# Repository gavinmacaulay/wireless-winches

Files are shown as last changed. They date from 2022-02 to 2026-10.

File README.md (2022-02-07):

# Wireless echosounder calibration winch system
 
This repository contains the manual for the Aqualyd Wireless Echosounder Calibration Winch System. A pdf of the latest version is available [here](https://github.com/gavinmacaulay/wireless-winches/blob/main/generated-docs/User%20and%20Technical%20Manual.pdf?raw=true).

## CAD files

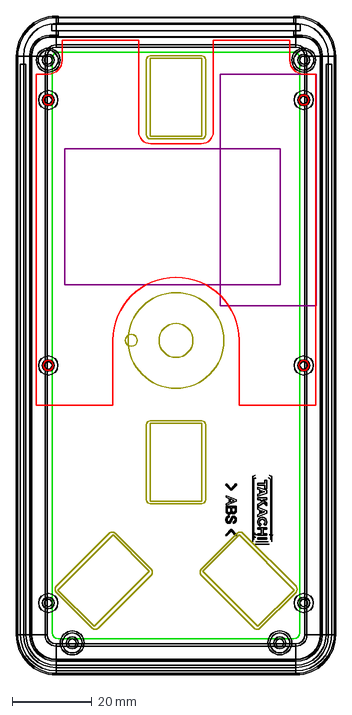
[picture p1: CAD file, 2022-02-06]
schematics/controller cut layout.dxf
80.0 x 165.0 mm

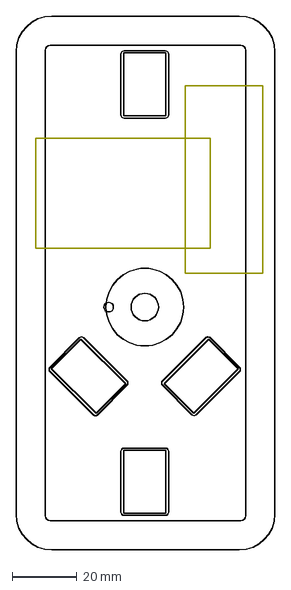
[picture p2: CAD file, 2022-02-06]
schematics/drill guidedxf.dxf
80.0 x 165.0 mm

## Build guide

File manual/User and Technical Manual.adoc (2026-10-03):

= Wireless echosounder calibration winch manual
:author: Aqualyd Limited
:email: gavin@aqualyd.nz
:revnumber: 1.5
:revdata: October 2026
:sectnums:
:doctype: book
:toc:
:toclevels: 4
:xrefstyle: short
:imagesdir: .
:chapter-label:
:!chapter-signifier:
:hide-uri-scheme:

[colophon]

(C) 2026 Aqualyd Limited +
341 Higgins Road +
Wakefield +
New Zealand

https://www.aqualyd.nz

The latest vesion of this manual is available on https://github.com/gavinmacaulay/wireless-winches.git[github].

= User Manual

This is the User Manual for the Aqualyd wireless echosounder calibration winch system and provides information on setting up and using the system.

== First-use setup

=== Batteries

The controller batteries (Nokia BL-5C or equivalent) may need to be installed. The steps to do this are:

1. Remove the lanyard and silicone case from the controllers.
2. Unscrew and remove the back of the case to expose the controller electronics.
3. Remove one of the screws that holds the strap that sits across the battery holder and rotate it out of the way.
4. Insert the battery, taking care to line up the battery terminals.
5. Rotate the strap into place and insert and tighten the screw.
6. Reinstall the controller case halves and screw them together.
7. Put the silicone cover back on and attach the lanyard strap.
8. Turn the controller on and check that an LED is flashing on the end of the controller case.

The winch batteries (Hikoki/Metabo HPT MultiVolt) slide vertically down onto the black clip on each winch. Press the gray buttons on the side of the batteries and pull up to remove a battery.

=== Installation of line on the reels

Line should be added to the reels so that the free end leaves from underneath the drum (and away from you) when viewing the unit with the yellow tube to your right. If the direction of the winches does not match the arrows on the controller, it is most likely that the line has been wound on the wrong way.

== Operating the system

=== Installing the winches and poles

Assemble each winch/pole as per this list:

1. Insert a telescopic pole into the yellow tube on each winch unit (orient the pole so that the brand name is uppermost), 
2. Extend the telescopic pole to the desired length,
3. Align the holes in the yellow tube and pole and insert the locking pin (the pole will extend about 200 mm inboard from the yellow tube),
4. Insert the supplied eye-bolt into the hole in the inboard end of the pole,
5. Attach a tie-down cord to each eye-bolt using the attached carabiner,
6. Insert a battery into the winch unit
7. Pay out line (using the controller) and lead it through the eye-bolt on the outboard end of the pole,
8. Secure the assembled unit to the vessel railing or bulwark rail and attach the tie-down cord to the vessel.

.Winch unit installed on a ship's railing showing hose clamps, securing pin, and attachment carabiner.
[[assembled_installed_winch_unit]]


The winch units are designed to be attached to a pipe or bulwark rail on a vessel (<<assembled_installed_winch_unit>>). A pipe attachment uses the supplied hose clamps to secure the aluminium section of the winch unit to the railing. A bulwakr rail attachment uses clamps (user supplied) to secure the winch units' plastic base or the aluminium section to the flat plate. 

The leverage from the extended poles is countered by the cord attachment from the inboard end of the pole to suitable point(s) on the vessel (e.g., a lower railing or gusset).

Each winch is numbered - place the winches in a location that fits with the layout of the numbered switches on the controller (<<hand_controller>>). For example, if one pole is at the bow of the vessel and the other two poles on port and starboard side, place winch 1 at the bow, winch 2 to port and winch 3 to starboard. Winch 1 holds the long pole.

To make it easy to relate the three winch switches to the winch locations, rotate the controller so that the switches approximately match the locations of the winches on the vessel when facing the echosounders' split-beam display. This will often mean holding the winch controller in a landscape orientation.

.Controller functions.
[[hand_controller]]


The controller and winches automatically form a wireless mesh network that relays commands from the controller to the winches even if all winches are not reachable directly from the controller. 

The controller can function as a range extender - to activate this, move the mode switch on the end of the controller to ``Extender``. The LED on the end of the unit will then flash red instead of green. Multiple range extenders can be used if necessary. When in extender mode, none of the winch controls on that controller are operational.

NOTE: When extending the telescopic poles do not extend each section beyond the red or blue band and ensure that each pole clip is closed after extending.

WARNING: Avoid rotating the winches by hand - instead, insert a battery and use the controller.

WARNING: The winch units are watertight, but the batteries are not. If using the winches in wet weather, secure a plastic bag over the battery/battery clip part of the winch (a thick rubber band works well to hold it in place).

=== Controlling the winches

Individual winches can be controlled using the three in/out switches on the controller. The speed of the winches is set with the dial. The slowest speed is 20 mm/s and the fastest 1 m/s. Multiple winches can be operated at the same time.

The in/out switches are configured to pay out line when the inner side of the switch is pressed - the arrows on the switches point in the direction that the sphere will move when viewed in a split-beam sphere position plot.

WARNING: Only use speeds in the red section of the dial when the weight on the winch is less than about 1.5 kg.

NOTE: It is easy to operate the winches without observing the winch and this can quickly cause unintentional damage to the winches or the poles (e.g., pulling a line too hard when the line is caught on the hull, paying out line when there is no tension on the line leading to tangles). Experience suggests that until the sphere is visible on the echosounder split-beam display, operation of the winches should be done while observing the winch/pole unit.

NOTE: If both controllers are turned on and set to ``controller`` mode, then both controllers will be sending potentially contradictory commands to the winches. A typical symptom of this is a winch moving in a struttering manner (i.e., one controler is telling the winch to rotate while the other is telling it to not rotate). 

=== Android app

.Screenshot from the Android app.
[[android_app]]
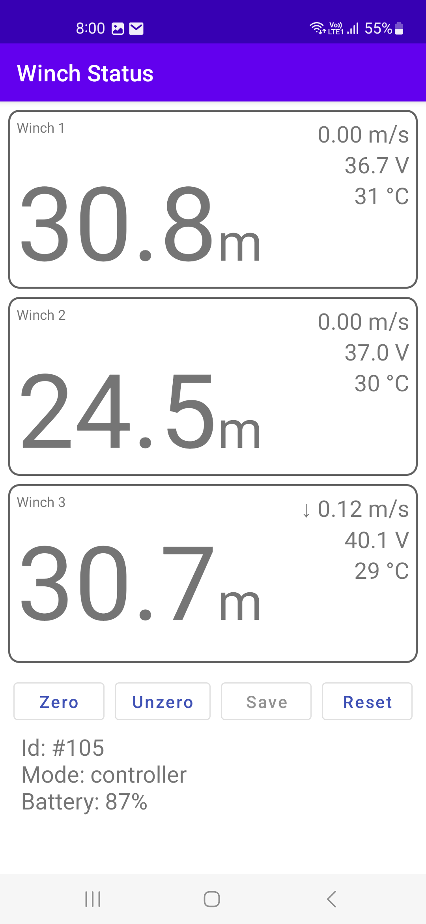
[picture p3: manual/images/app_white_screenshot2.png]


An app is available on the Google Play Store under the name ``Aqualyd Winch Status``, via this https://play.google.com/store/apps/details?id=nz.aqualyd.winchStatus[URL], or the QR code below. 

The app requires an Android device running version 9 of Android or later that also supports Bluetooth. The app does not provide a way to control the winches. 

The app shows line out, line speed, battery voltage, and internal winch temperature for each winch (<<android_app>>). Controller battery charge, mode, and serial number are also shown. The winch battery voltage number turns red when a battery need charging.

The displayed line out values can be zeroed (using the ``Zero`` button) and restored with the ``Unzero`` button. The winches will reset their line out counters when the ``Reset`` button in pressed. This cannot be undone. The winches remember the current line out value even when the batteries are removed, so a ``Reset`` is the only way to force the winches' line counters to be zero. The ``Save`` button is not yet implemented, but will eventually allow for saving (and restoring) of line out values along with with a timestamp and label. 

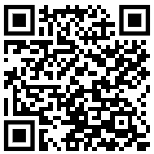
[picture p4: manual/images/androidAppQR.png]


=== Monitor device

Connect a Monitor device to a USB port, whereupon winch and controller status messages will be output on a virtual serial port. Information on Monitor devices is given in <<Monitor Xbee device>> and the format of the messages they produce are detailed in <<_communication>>. Multiple Monitor devices can be used at the same time. Monitor devices are not part of the standard calibration kit.

=== Charging the batteries 

The controller contains a rechargable battery. To charge this, connect a micro USB cable to the unit and to a USB power supply (the USB port on a computer is fine - there is also a USB port on the Hikoki/Metabo HPT charger) and *turn the controller on*. Charging a completely flat battery will take about 4 hours and a fully charged battery will work for about 20 hours.

Note that the controller will be operating and transmitting whenever USB power is suppled, but will not charge the battery until the power switch is turned on (the on/off switch connects or disconnects the battery from the system - it does not affect supply of USB power to the controller's electronics). This means that a controller with a flat, faulty, or absent battery can be used normally by connecting USB power - it will operate as per normal and charge the battery if present.

The winch batteries are charged with the supplied Hikoki/Metabo HPT charger. It takes about 40 minutes to fully charge an empty winch battery. 

= Technical Manual

This is the Technical Manual for the Aqualyd wireless echosounder calibration winch system. This section provides details on how the system works, the main components, and information to assist with repair and modifications of the system.

== System description

The overall system consists of two controllers and three winches. Communication between these units occurs via a 2.4 GHz mesh network, provided by Digi XBee3 radio modules. The controller broadcasts a message at 10 Hz that contains the state of all three in/out switches (up, down, stationary) and the potentiometer (0-255). Each winch unit listens to these messages, picks out the relevant in/out switch state and sends speed and direction commands to the motor controller, which operates the stepper model to rotate the winch drum. The relationship between the speed setting on the controller and the actual motor speed is determined by calculations done by the code running in the winch unit. At every 5^th^ broadcast, each winch replies with winch status information which the controller sends via bluetooth to the Android app.

The system is provided in three parts: 1) a transit/storage case that contains the controllers and three winch units, 2) a transit/storage case with the winch batteries and chargers, and 3) a tube that contains the three poles (<<whole_system>>). 

.Supplied winch system showing (left) the transit case with included winches and controllers, (centre) the tube containing the poles, and (right) the battery and charger case.
[[whole_system]]
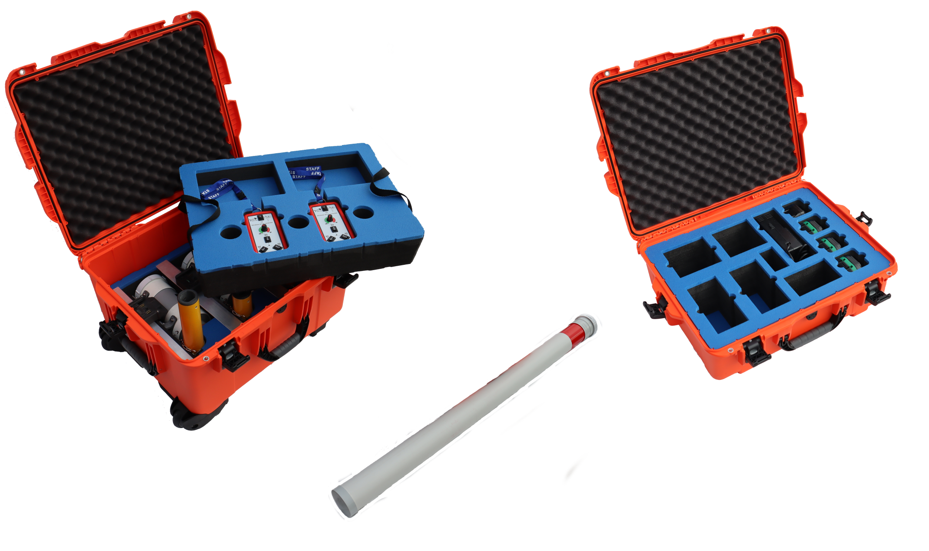
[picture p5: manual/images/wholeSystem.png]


=== Winches

The motors are of NEMA 23 size with an integrated 4.25:1 planetary gearbox, supplied by StepperOnline (model 23HS30-2804S-PG4). The motor is driven from a Pololu Tic T246 motor controller which is controlled via I2C (serial in earlier models) communication with a microPython programm running on the XBee3 radio module in each winch unit. 

The acceleration and decceleration applied when the motor speed is changed is determined by a programmable setting in the Tic T246, as well as the maximum motor speed, and command timeout when no controller messages are received. Each unit stores the current line out value in non-volatile RAM and recalls that on power up so that battery swaps preserve the line out value.

The winches were designed to hold a 6 kg load and are able to lift and lower 6 kg at slow speeds. Operation at higher speeds is only possible with lighter loads. The winch units operate with a 10-40 V DC input, but at least 36 V is needed to achieve sufficient motor torque to hold a 6 kg line load. 

=== Controller

The controller contains a Digi XBee3 radio module, switches, a potentiometer, a rechargable battery, and a PCB that contains a MAX17048 battery status chip, LED's, and a mode switch. The XBee3 is integrated in a SparkFun Thing Plus XBee3 board (P/N WRL-15454) which provides power to the XBee3 via USB or a Lithium-Polymer battery. Battery management circuitry is also included that will charge the battery when USB power is provided.

The mode switch on the controller sets whether the controller operates as a controller or as a range extender. In range extender mode the winch controls are disabled.

=== Software

The controller runs a microPython program on the XBee3 module to translate buttons presses and speed setting into the message that is broadcast to the winches. The XBee3 in each winch also runs a microPython program that receives these messages, decodes them and sends motor speed and direction commands to the motor controller. The code that runs on these XBee3 modules is available on https://github.com/gavinmacaulay/wireless-winches.git[github].

Uploading the microPython code to the XBee3 module in the controller is done via the USB connector on the controller. Uploading to the XBee3 module in the winches requires a separate board that provides serial communication access to the Xbee3 (e.g. an XBee Grove Development Board) or a USB to uart adapter to a serial connector on the device. Modifying the parameters in the Pololu motor controller can be done via the USB connector on the Pololu unit. 

=== Changing winch identification

Changing the winch identification may be necessary when replacing a faulty winch. 

Each winch has an identification number (1, 2, 3). This is used by each winch to select the appropriate part of the message sent by the controller. This number is stored in the NI parameter in the XBee3 unit and is read when powering up. Changing this number can be done using the Digi XCTU software (via USB) or the Digi XBee mobile app (via Bluetooth). The Bluetooth password is *aqualyd*.

Note that the controller only sends out messages to winches with identification codes of 1, 2, or 3. If the winch NI parameter is set to any other value that winch will not act on any commands from the controller.

=== Poles

The poles are telescopic and made either of a 50/50 mix of carbon fibre and fibreglass or 100% carbon fibre (depends on the model). They are originally made for window washing and replacements are readily available from cleaning suppliers.

== Communication

=== Controller-produced messages

The controller broadcasts a message to the winches, consisting of a single string containing six ASCII characters. Optionally, the message can contain two extra characters that are used to configure a winch. The meaning of the characters are:

* Characters one to three specify the required winch motion for each winch (first character for winch 1, second for winch 2 and the third for winch 3). The value of each character is `0`, `1`, or `2`. `0` means to stop the winch, `1` to pay out line, and `2` to take in line. 
* Characters four to six are interpreted as an integer number between 0 and 255 that gives the position of the speed dial. 
* Character 7 is a command code. The only value accepted to date is `z`, used to tell a winch to reset to zero the line out counter. If `z` is sent, character 8 specifies which winch the reset applies to (i.e., `1`, `2`, or `3`). When the line out is reset, that winch will stop rotating, the line out value will be set to zero, a status message will be sent to the Android app, and then any speed/direction commands in the message for that winch will be acted upon.

Some examples: 

* `000105` will ensure that all winches are stopped. The speed potentiometer is set to a little under half speed.
* `011000` will cause winches 2 and 3 to pay line out at the minimum speed.
* `20125500` will cause winch 1 to take line in and winch 3 to pay line out, both at the maximum speed. Winch 2 will not rotate. As the 7th character is not `z`, the last two characters will have no effect.
* `201128z2` will cause the line counter for winch 2 to be zeroed, winch 1 to take line in, and winch 3 to pay line out, both at half speed.

The controller also sends a winch status message to the Android app and any active Monitor devices in the form of a comma separated ASCII string in the form:

`0,id,mode,v.v,s.s,r.r`

where the fields are:

.Controller status message format.
[%autowidth]
|===
|Field|Content|Decimal places|Units
|id|Serial number of the controller|string|
|mode|Mode of the controller|string|
|v.v|Controller battery voltage|2|V
|s.s|Controller battery charge|1|%
|r.r|Controller battery rate of (dis)charge|1|%/hour
|===

The `0` in the first location is used by the app to separate controller messages from winch messages (which always start with the winch identification number: 1, 2, or 3).

=== Winch-produced messages

A winch status message is sent by each winch unit back to the controller, which forwards it out over the Bluetooth Low Energy communication link (using the Xbee3 User Data Frame mechanism). An Android app is available that uses these messages to show winch status information. The status message is also sent to any active Monitor Xbee devices. This message is a comma separated ASCII string in the form:

`w,v.v,t,pp.pp,ss.ss,V`

where the fields are:

.Winch status message format.
[%autowidth]
|===
|Field|Content|Decimal places|Units
|w|Winch identification (1, 2, or 3)||
|v.v|Battery voltage|1|V
|t|Winch internal temperature|0|&#176;C
|pp.pp|Line paid out (can include leading negative sign)|2|m
|ss.ss|Line speed (can include leading negative sign)|2|m s^-1^
|V|Winch version idenfication (optional)|string|
|===

A negative line paid out value indicates the line has been taken in more than paid out. A negative line speed indicates the line is being taken in. The winch version idenfication is used by the Andoid app to modify its' user interface to match the capabilities of the winch. It is optional and it and the preceeding comma are not produced by earlier versions of the winch code. Currently used values are:

.Winch version information.
[%autowidth]
|===
|Value|Comms with motor controller|Remembers line out
|1|UART|No
|2|UART|Yes
|3|i2c|Yes
|===

=== App-produced messages

The Android app can send two-byte ASCII strings to the controller, which appends them to the messages sent to the winches (these are the 7th and 8th characters in the controller-produced message). This is currently used to tell the winches to reset their line counters.

=== Monitor Xbee device

A Monitor Xbee is a device that receives winch and controller status messages and outputs them on a USB/serial port - this is independent of the controller and Android app. Multiple Monitor devices can operate simultaneously, each outputting the winch and controller status messages. The Sparkfun Thing Plus Xbee is recommended for use as a Monitor device as it inorporates a USB connection that provides both serial data and a power supply for the Xbee. 

Three example winch status display programs are provided:

* https://github.com/gavinmacaulay/wireless-winches/blob/main/code/status_display_gui.py[Python code] that produces a simple GUI display of the winch information
* https://github.com/gavinmacaulay/wireless-winches/blob/main/code/status_display.py[Python code] that produces a terminal-based text display of the winch information
* https://github.com/gavinmacaulay/wireless-winches/blob/main/code/status_display_web.html[HTML code] for web browsers that support the https://developer.mozilla.org/en-US/docs/Web/API/Web_Serial_API[Web Serial API] (mainly Chromium-based ones, such as Chome, Edge, and Opera)

You can also write your own code to display the status messages or use dashboard software that can parse data from a serial port (e.g., https://github.com/Serial-Studio/Serial-Studio[Serial-Studio]).

The virtual serial port should be set to 9600/8/N/1 and is provided by a Silicon Labs CP210x USB to UART bridge device on all controllers that use the Sparkfun Thing Plus Xbee radio unit.

[appendix]
== Specifications

[%autowidth,cols="<,>,>"]
|===
|Parameter|Value|Units
|Maximum line speed|1|m/s
|Minimum line speed|0.02|m/s
|||
|Maximum stationary load|6|kg
|Maximum load at 1 m/s line speed|~1.5|kg
|Maximum load at 0.5 m/s line speed|~3|kg
|||
|Winch supply voltage|10-40|V DC
|Winch supply voltage for design performance|36|V DC
|||
|Current usage at 6 kg load, 0.02 m/s|<0.1|A
|Peak current usage at 3 kg load, 0.5 m/s|0.07|A
|Recommended minimum current rating of power supply|1.5|A
|Maximum current usage based on motor specs|3.4|A
|||
|Wireless communication protocol|XBee DigiMesh|
|DigiMesh network identification|0xA1A1|
|DigiMesh network channel|0x1A|
|DigiMesh wireless channel|26 (2480 MHz)|
|||
|Controller battery|Nokia BL-5C|
|Battery chemistry|Lithium Ion|
|Battery voltage|3.7|V
|Battery rating|1.05|Ah
|Battery rating|3.8|Wh
|||
|Winch battery|Hikoki/Metabo HPT MultiVolt BSL36A18X|
|Battery chemistry|Lithium Ion|
|Battery voltage|36|V
|Battery rating|2.5|Ah
|Battery rating|90|Wh
|===

[appendix]
== Supplied Parts
A wireless system consists of the following components:

[%autowidth]
|===
|Component|Quantity
|Transit/storage case (Nanuk 960) for winches and controllers with fitted foam|1
|Transit/storage case (Nanuk 945) for batteries and charger with fitted foam|1
|Transit/storage tube for poles|1
|Winch unit (for short pole)|2
|Winch unit (for long pole)|1
|Short pole|2
|Long pole|1
|Pole attachment cord with carabiner|4
|Pole attachment eyebolt|3
|Winch batteries|4
|Winch battery charger|1
|Controller|2
|Controller charging cord (USB)|1
|User & Technical manual (online)|1
|Hose clamps (46-70 mm diameter)|6
|Hose clamp nut driver with 6, 7, and 8 mm sockets|1
|===

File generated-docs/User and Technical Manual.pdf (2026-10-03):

# Wireless echosounder calibration winch manual

### Aqualyd Limited

Version 1.5

# Table of Contents

### © 2026 Aqualyd Limited 341 Higgins Road Wakefield New Zealand

www.aqualyd.nz

The latest vesion of this manual is available on github. (https://github.com/gavinmacaulay/wireless-winches.git)

# User Manual

This is the User Manual for the Aqualyd wireless echosounder calibration winch system and provides information on setting up and using the system.

# 1. First-use setup

# 1.1. Batteries

The controller batteries (Nokia BL-5C or equivalent) may need to be installed. The steps to do this are:

1. Remove the lanyard and silicone case from the controllers.
2. Unscrew and remove the back of the case to expose the controller electronics.
3. Remove one of the screws that holds the strap that sits across the battery holder and rotate it out of the way.
4. Insert the battery, taking care to line up the battery terminals.
5. Rotate the strap into place and insert and tighten the screw.
6. Reinstall the controller case halves and screw them together.
7. Put the silicone cover back on and attach the lanyard strap.
8. Turn the controller on and check that an LED is flashing on the end of the controller case.

The winch batteries (Hikoki/Metabo HPT MultiVolt) slide vertically down onto the black clip on each winch. Press the gray buttons on the side of the batteries and pull up to remove a battery.

# 1.2. Installation of line on the reels

Line should be added to the reels so that the free end leaves from underneath the drum (and away from you) when viewing the unit with the yellow tube to your right. If the direction of the winches does not match the arrows on the controller, it is most likely that the line has been wound on the wrong way.

# 2. Operating the system

# 2.1. Installing the winches and poles

Assemble each winch/pole as per this list:

1. Insert a telescopic pole into the yellow tube on each winch unit (orient the pole so that the brand name is uppermost),
2. Extend the telescopic pole to the desired length,
3. Align the holes in the yellow tube and pole and insert the locking pin (the pole will extend about 200 mm inboard from the yellow tube),
4. Insert the supplied eye-bolt into the hole in the inboard end of the pole,
5. Attach a tie-down cord to each eye-bolt using the attached carabiner,
6. Insert a battery into the winch unit
7. Pay out line (using the controller) and lead it through the eye-bolt on the outboard end of the pole,
8. Secure the assembled unit to the vessel railing or bulwark rail and attach the tie-down cord to the vessel.

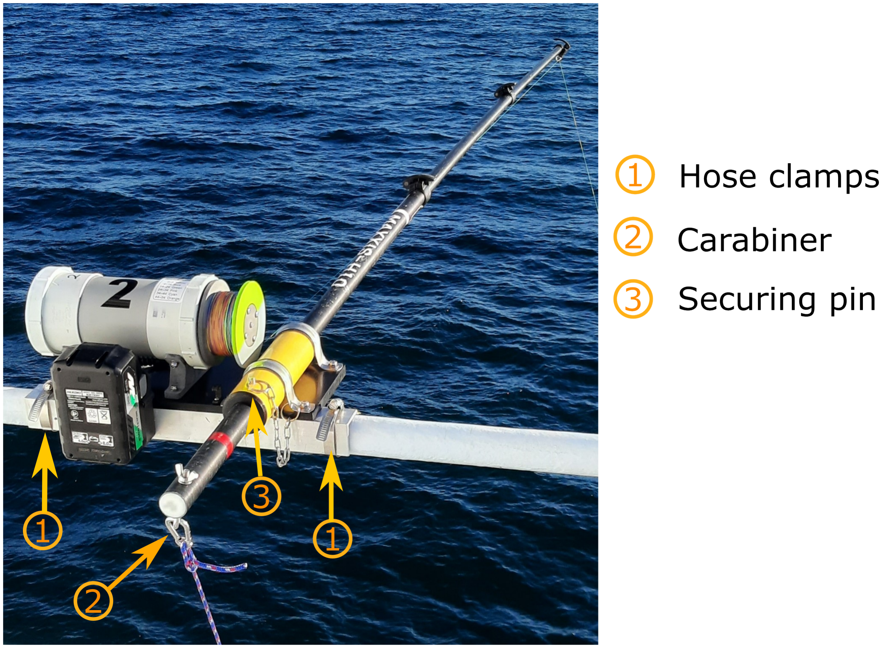
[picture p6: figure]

Figure 1. Winch unit installed on a ship’s railing showing hose clamps, securing pin, and attachment carabiner.

The winch units are designed to be attached to a pipe or bulwark rail on a vessel (Figure 1). A pipe attachment uses the supplied hose clamps to secure the aluminium section of the winch unit to the railing. A bulwakr rail attachment uses clamps (user supplied) to secure the winch units' plastic base or the aluminium section to the flat plate.

The leverage from the extended poles is countered by the cord attachment from the inboard end of the pole to suitable point(s) on the vessel (e.g., a lower
railing or gusset).

Each winch is numbered - place the
winches in a location that fits with the layout of the numbered switches on the controller (Figure 2). For example, if one pole is at the bow of the vessel and the other two poles on port and starboard side, place winch 1 at the bow, winch 2 to port and winch 3 to starboard. Winch 1 holds the long pole.

To make it easy to relate the three winch switches to the winch locations, rotate the controller so that the switches approximately match the locations of the winches on the vessel when facing the echosounders' split-beam display. This will often mean holding the winch controller in a landscape orientation.

2
3

### On/off Speed Direction

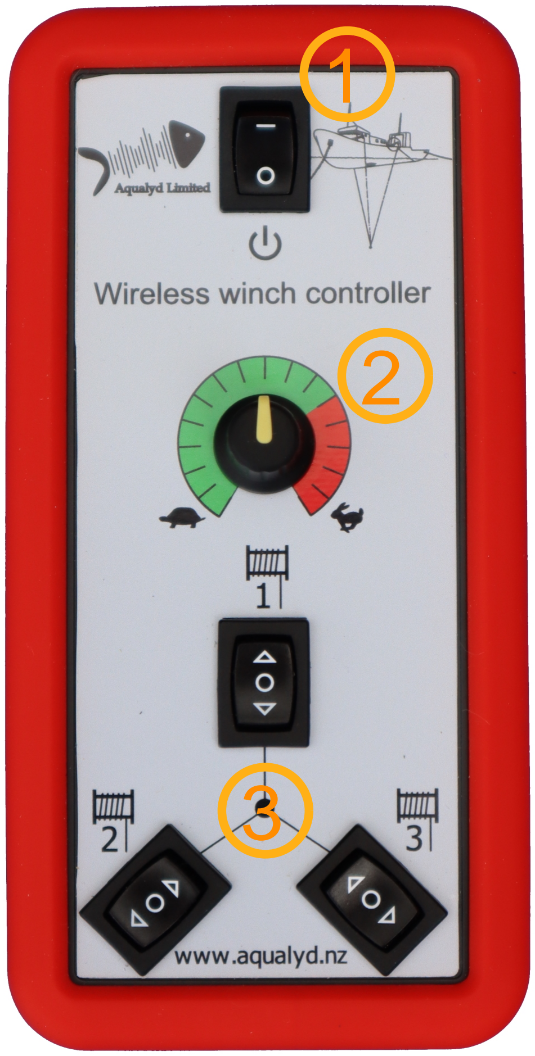
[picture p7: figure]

Figure 2. Controller functions.

The controller and winches automatically form a wireless mesh network that relays commands from the controller to the winches even if all winches are not reachable directly from the controller.

The controller can function as a range extender - to activate this, move the mode switch on the end of the controller to Extender. The LED on the end of the unit will then flash red instead of green. Multiple range extenders can be used if necessary. When in extender mode, none of the winch controls on that controller are operational.

NOTE

When extending the telescopic poles do not extend each section beyond the red or blue band and ensure that each pole clip is closed after extending.

WARNING

Avoid rotating the winches by hand - instead, insert a battery and use the controller.

WARNING

The winch units are watertight, but the batteries are not. If using the winches in wet weather, secure a plastic bag over the battery/battery clip part of the winch (a thick rubber band works well to hold it in place).

# 2.2. Controlling the winches

Individual winches can be controlled using the three in/out switches on the controller. The speed of the winches is set with the dial. The slowest speed is 20 mm/s and the fastest 1 m/s. Multiple winches can be operated at the same time.

The in/out switches are configured to pay out line when the inner side of the switch is pressed - the arrows on the switches point in the direction that the sphere will move when viewed in a split-beam sphere position plot.

WARNING

Only use speeds in the red section of the dial when the weight on the winch is less than about 1.5 kg.

NOTE

It is easy to operate the winches without observing the winch and this can quickly cause unintentional damage to the winches or the poles (e.g., pulling a line too hard when the line is caught on the hull, paying out line when there is no tension on the line leading to tangles). Experience suggests that until the sphere is visible on the echosounder split-beam display, operation of the winches should be done while observing the winch/pole unit.

NOTE If both controllers are turned on and set to controller mode, then both controllers will be sending potentially contradictory commands to the winches. A typical symptom of this is a winch moving in a struttering manner (i.e., one controler is telling the winch to rotate while the other is telling it to not rotate).

# 2.3. Android app

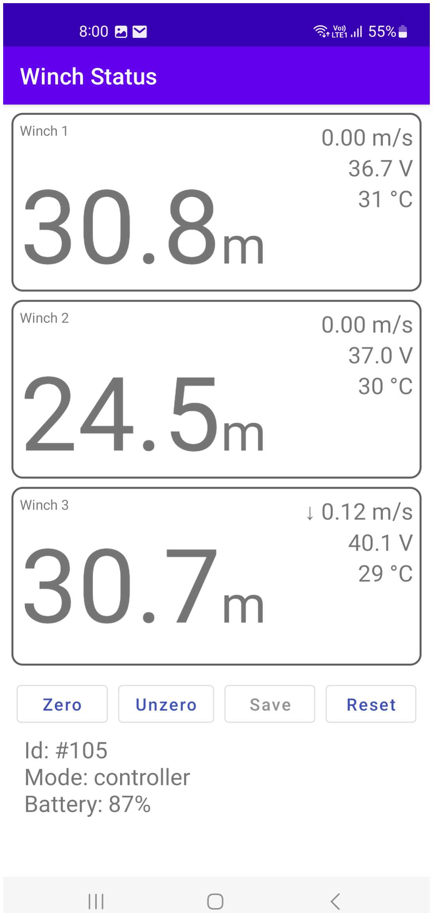
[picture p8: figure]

Figure 3. Screenshot from the Android app.

An app is available on the Google Play Store under the name Aqualyd Winch Status, via this URL, (https://play.google.com/store/apps/details?id=nz.aqualyd.winchStatus) or the QR code below.

The app requires an Android device running version 9 of Android or later that also supports Bluetooth. The app does not provide a way to control the winches.

The app shows line out, line speed, battery voltage, and internal winch temperature for each winch (Figure 3). Controller battery charge, mode, and serial number are also shown. The winch battery voltage number turns red when a battery need charging.

The displayed line out values can be zeroed (using the Zero button) and restored with the Unzero button. The winches will reset their line out counters when the Reset button in pressed. This cannot be undone. The winches remember the current line out value even when the batteries are removed, so a Reset is the only way to force the winches' line counters to be zero. The Save button is not yet implemented, but will eventually allow for saving (and restoring) of line out values along with with a timestamp and label.

# 2.4. Monitor device

Connect a Monitor device to a USB port, whereupon winch and controller status messages will be output on a virtual serial port. Information on Monitor devices is given in Section 4.4 and the format of the messages they produce are detailed in Chapter 4. Multiple Monitor devices can be used at the same time. Monitor devices are not part of the standard calibration kit.

# 2.5. Charging the batteries

The controller contains a rechargable battery. To charge this, connect a micro USB cable to the unit and to a USB power supply (the USB port on a computer is fine - there is also a USB port on the Hikoki/Metabo HPT charger) and turn the controller on. Charging a completely flat battery will take about 4 hours and a fully charged battery will work for about 20 hours.

Note that the controller will be operating and transmitting whenever USB power is suppled, but will not charge the battery until the power switch is turned on (the on/off switch connects or disconnects the battery from the system - it does not affect supply of USB power to the controller’s electronics). This means that a controller with a flat, faulty, or absent battery can be used normally by connecting USB power - it will operate as per normal and charge the battery if present.

The winch batteries are charged with the supplied Hikoki/Metabo HPT charger. It takes about 40 minutes to fully charge an empty winch battery.

# Technical Manual

This is the Technical Manual for the Aqualyd wireless echosounder calibration winch system. This section provides details on how the system works, the main components, and information to assist with repair and modifications of the system.

# 3. System description

The overall system consists of two controllers and three winches. Communication between these units occurs via a 2.4 GHz mesh network, provided by Digi XBee3 radio modules. The controller broadcasts a message at 10 Hz that contains the state of all three in/out switches (up, down, stationary) and the potentiometer (0-255). Each winch unit listens to these messages, picks out the relevant in/out switch state and sends speed and direction commands to the motor controller, which operates the stepper model to rotate the winch drum. The relationship between the speed setting on the controller and the actual motor speed is determined by calculations done by the code running in the winch unit. At every 5th broadcast, each winch replies with winch status information which the controller sends via bluetooth to the Android app.

The system is provided in three parts: 1) a transit/storage case that contains the controllers and three winch units, 2) a transit/storage case with the winch batteries and chargers, and 3) a tube that contains the three poles (Figure 4).

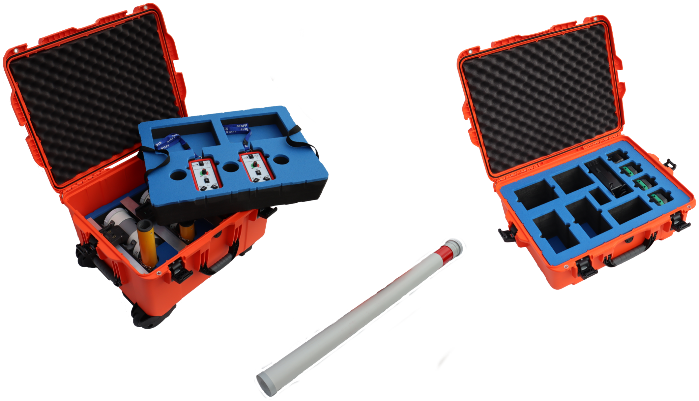
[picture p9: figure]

Figure 4. Supplied winch system showing (left) the transit case with included winches and controllers, (centre) the tube containing the poles, and (right) the battery and charger case.

# 3.1. Winches

The motors are of NEMA 23 size with an integrated 4.25:1 planetary gearbox, supplied by StepperOnline (model 23HS30-2804S-PG4). The motor is driven from a Pololu Tic T246 motor controller which is controlled via I2C (serial in earlier models) communication with a microPython programm running on the XBee3 radio module in each winch unit.

The acceleration and decceleration applied when the motor speed is changed is determined by a programmable setting in the Tic T246, as well as the maximum motor speed, and command timeout when no controller messages are received. Each unit stores the current line out value in non-volatile RAM and recalls that on power up so that battery swaps preserve the line out value.

The winches were designed to hold a 6 kg load and are able to lift and lower 6 kg at slow speeds. Operation at higher speeds is only possible with lighter loads. The winch units operate with a 10-40 V DC input, but at least 36 V is needed to achieve sufficient motor torque to hold a 6 kg line load.

# 3.2. Controller

The controller contains a Digi XBee3 radio module, switches, a potentiometer, a rechargable battery, and a PCB that contains a MAX17048 battery status chip, LED’s, and a mode switch. The XBee3 is integrated in a SparkFun Thing Plus XBee3 board (P/N WRL-15454) which provides power to the XBee3 via USB or a Lithium-Polymer battery. Battery management circuitry is also included that will charge the battery when USB power is provided.

The mode switch on the controller sets whether the controller operates as a controller or as a range extender. In range extender mode the winch controls are disabled.

# 3.3. Software

The controller runs a microPython program on the XBee3 module to translate buttons presses and speed setting into the message that is broadcast to the winches. The XBee3 in each winch also runs a microPython program that receives these messages, decodes them and sends motor speed and direction commands to the motor controller. The code that runs on these XBee3 modules is available on github. (https://github.com/gavinmacaulay/wireless-winches.git)

Uploading the microPython code to the XBee3 module in the controller is done via the USB connector on the controller. Uploading to the XBee3 module in the winches requires a separate board that provides serial communication access to the Xbee3 (e.g. an XBee Grove Development Board) or a USB to uart adapter to a serial connector on the device. Modifying the parameters in the Pololu motor controller can be done via the USB connector on the Pololu unit.

# 3.4. Changing winch identification

Changing the winch identification may be necessary when replacing a faulty winch.

Each winch has an identification number (1, 2, 3). This is used by each winch to select the appropriate part of the message sent by the controller. This number is stored in the NI parameter in the XBee3 unit and is read when powering up. Changing this number can be done using the Digi XCTU software (via USB) or the Digi XBee mobile app (via Bluetooth). The Bluetooth password is aqualyd.

Note that the controller only sends out messages to winches with identification codes of 1, 2, or 3. If the winch NI parameter is set to any other value that winch will not act on any commands from the controller.

# 3.5. Poles

The poles are telescopic and made either of a 50/50 mix of carbon fibre and fibreglass or 100% carbon fibre (depends on the model). They are originally made for window washing and replacements are readily available from cleaning suppliers.

# 4. Communication

# 4.1. Controller-produced messages

The controller broadcasts a message to the winches, consisting of a single string containing six ASCII characters. Optionally, the message can contain two extra characters that are used to configure a winch. The meaning of the characters are:

- Characters one to three specify the required winch motion for each winch (first character for winch 1, second for winch 2 and the third for winch 3). The value of each character is 0, 1, or 2. 0 means to stop the winch, 1 to pay out line, and 2 to take in line.
- Characters four to six are interpreted as an integer number between 0 and 255 that gives the position of the speed dial.
- Character 7 is a command code. The only value accepted to date is z, used to tell a winch to reset to zero the line out counter. If z is sent, character 8 specifies which winch the reset applies to (i.e., 1, 2, or 3). When the line out is reset, that winch will stop rotating, the line out value will be set to zero, a status message will be sent to the Android app, and then any speed/direction commands in the message for that winch will be acted upon.

Some examples:

- 000105 will ensure that all winches are stopped. The speed potentiometer is set to a little under half speed.
- 011000 will cause winches 2 and 3 to pay line out at the minimum speed.
- 20125500 will cause winch 1 to take line in and winch 3 to pay line out, both at the maximum speed. Winch 2 will not rotate. As the 7th character is not z, the last two characters will have no effect.
- 201128z2 will cause the line counter for winch 2 to be zeroed, winch 1 to take line in, and winch 3 to pay line out, both at half speed.

The controller also sends a winch status message to the Android app and any active Monitor devices in the form of a comma separated ASCII string in the form:

0,id,mode,v.v,s.s,r.r

where the fields are:

Table 1. Controller status message format.
Field | Content | Decimal places | Units
id | Serial number of the controller | string
mode | Mode of the controller | string
v.v | Controller battery voltage | 2 | V
s.s | Controller battery charge | 1 | %
r.r | Controller battery rate of (dis)charge | 1 | %/hour

The 0 in the first location is used by the app to separate controller messages from winch messages (which always start with the winch identification number: 1, 2, or 3).

# 4.2. Winch-produced messages

A winch status message is sent by each winch unit back to the controller, which forwards it out over the Bluetooth Low Energy communication link (using the Xbee3 User Data Frame mechanism). An Android app is available that uses these messages to show winch status information. The status message is also sent to any active Monitor Xbee devices. This message is a comma separated ASCII string in the form:

w,v.v,t,pp.pp,ss.ss,V

where the fields are:

Table 2. Winch status message format.
Field | Content | Decimal places | Units
w | Winch identification (1, 2, or 3)
v.v | Battery voltage | 1 | V
t | Winch internal temperature | 0 | °C
pp.pp | Line paid out (can include leading negative sign) | 2 | m
ss.ss | Line speed (can include leading negative sign) | 2 | m s⁻¹
V | Winch version idenfication (optional) | string

A negative line paid out value indicates the line has been taken in more than paid out. A negative line speed indicates the line is being taken in. The winch version idenfication is used by the Andoid app to modify its' user interface to match the capabilities of the winch. It is optional and it and the preceeding comma are not produced by earlier versions of the winch code. Currently used values are:

Table 3. Winch version information.
Value | Comms with motor controller | Remembers line out
1 | UART | No
2 | UART | Yes
3 | i2c | Yes

# 4.3. App-produced messages

The Android app can send two-byte ASCII strings to the controller, which appends them to the messages sent to the winches (these are the 7th and 8th characters in the controller-produced message). This is currently used to tell the winches to reset their line counters.

# 4.4. Monitor Xbee device

A Monitor Xbee is a device that receives winch and controller status messages and outputs them on a USB/serial port - this is independent of the controller and Android app. Multiple Monitor devices can operate simultaneously, each outputting the winch and controller status messages. The Sparkfun Thing Plus Xbee is recommended for use as a Monitor device as it inorporates a USB connection that provides both serial data and a power supply for the Xbee.

Three example winch status display programs are provided:

- Python code (https://github.com/gavinmacaulay/wireless-winches/blob/main/code/status_display_gui.py) that produces a simple GUI display of the winch information
- Python code (https://github.com/gavinmacaulay/wireless-winches/blob/main/code/status_display.py) that produces a terminal-based text display of the winch information
- HTML code (https://github.com/gavinmacaulay/wireless-winches/blob/main/code/status_display_web.html) for web browsers that support the Web Serial API (https://developer.mozilla.org/en-US/docs/Web/API/Web_Serial_API) (mainly Chromium-based ones, such as Chome, Edge, and Opera)

You can also write your own code to display the status messages or use dashboard software that can parse data from a serial port (e.g., Serial-Studio). (https://github.com/Serial-Studio/Serial-Studio)

The virtual serial port should be set to 9600/8/N/1 and is provided by a Silicon Labs CP210x USB to UART bridge device on all controllers that use the Sparkfun Thing Plus Xbee radio unit.

# Appendix A: Specifications

Parameter | Value | Unit s
Maximum line speed | 1 | m/s
Minimum line speed | 0.02 | m/s
Maximum stationary load | 6 | kg
Maximum load at 1 m/s line speed | ~1.5 | kg
Maximum load at 0.5 m/s line speed | ~3 | kg
Winch supply voltage | 10-40 | V DC
Winch supply voltage for design performance | 36 | V DC
Current usage at 6 kg load, 0.02 m/s | <0.1 | A
Peak current usage at 3 kg load, 0.5 m/s | 0.07 | A
Recommended minimum current rating of power supply | 1.5 | A
Maximum current usage based on motor specs | 3.4 | A
Wireless communication protocol | XBee DigiMesh
DigiMesh network identification | 0xA1A1
DigiMesh network channel | 0x1A
DigiMesh wireless channel | 26 (2480 MHz)
Controller battery | Nokia BL-5C
Battery chemistry | Lithium Ion
Battery voltage | 3.7 | V
Battery rating | 1.05 | Ah
Battery rating | 3.8 | Wh
Winch battery | Hikoki/Metabo HPT MultiVolt BSL36A18X
Battery chemistry | Lithium Ion
Battery voltage | 36 | V
Battery rating | 2.5 | Ah
Battery rating | 90 | Wh

# Appendix B: Supplied Parts

A wireless system consists of the following components:

Component | Quantity
Transit/storage case (Nanuk 960) for winches and controllers with fitted foam | 1
Transit/storage case (Nanuk 945) for batteries and charger with fitted foam | 1
Transit/storage tube for poles | 1
Winch unit (for short pole) | 2
Winch unit (for long pole) | 1
Short pole | 2
Long pole | 1
Pole attachment cord with carabiner | 4
Pole attachment eyebolt | 3
Winch batteries | 4
Winch battery charger | 1
Controller | 2
Controller charging cord (USB) | 1
User & Technical manual (online) | 1
Hose clamps (46-70 mm diameter) | 6
Hose clamp nut driver with 6, 7, and 8 mm sockets | 1

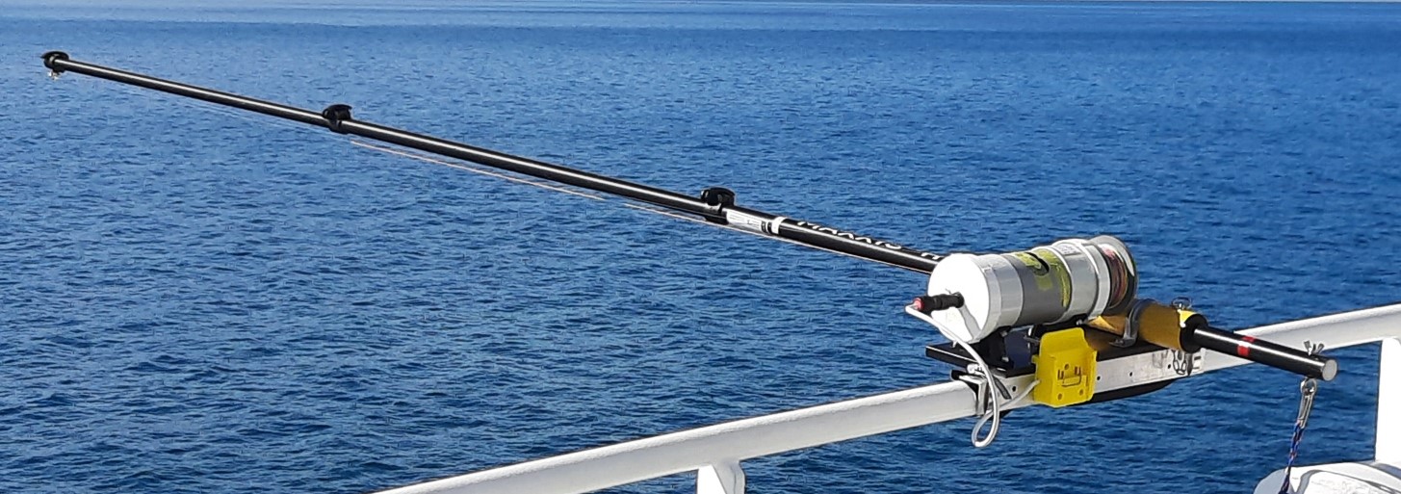
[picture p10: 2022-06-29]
manual/images/port location.jpg

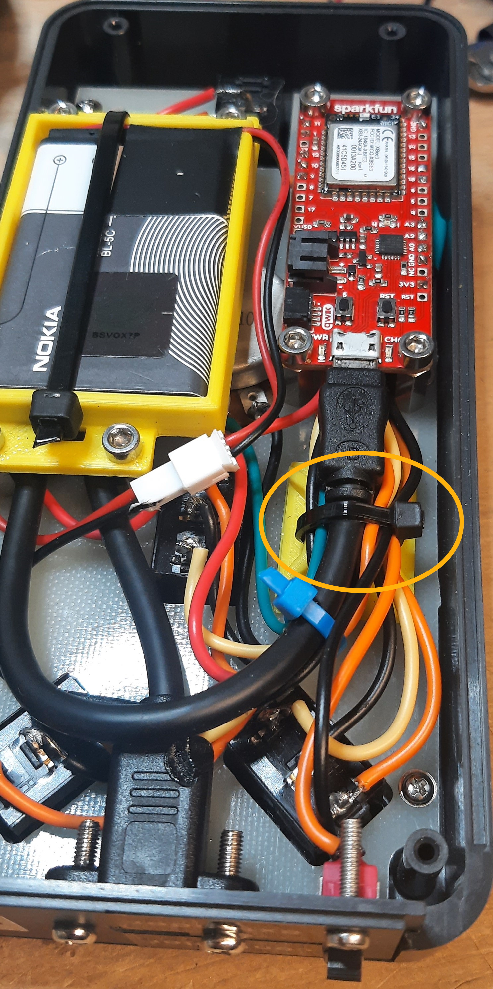
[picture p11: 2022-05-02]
manual/images/controller wiring done.jpg

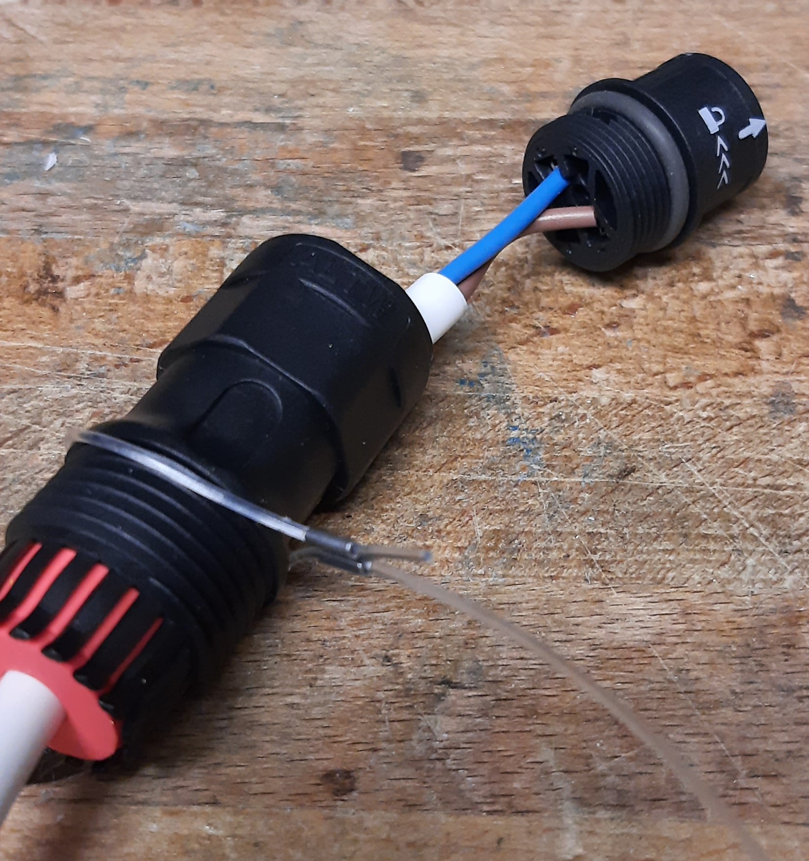
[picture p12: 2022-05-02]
manual/images/battery connector.jpg

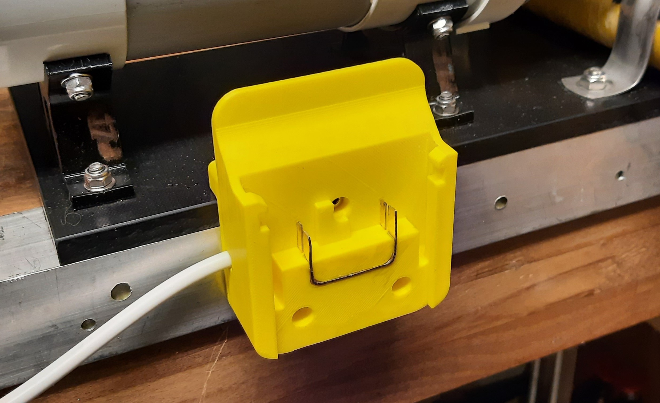
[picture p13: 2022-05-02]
manual/images/battery bracket.jpg

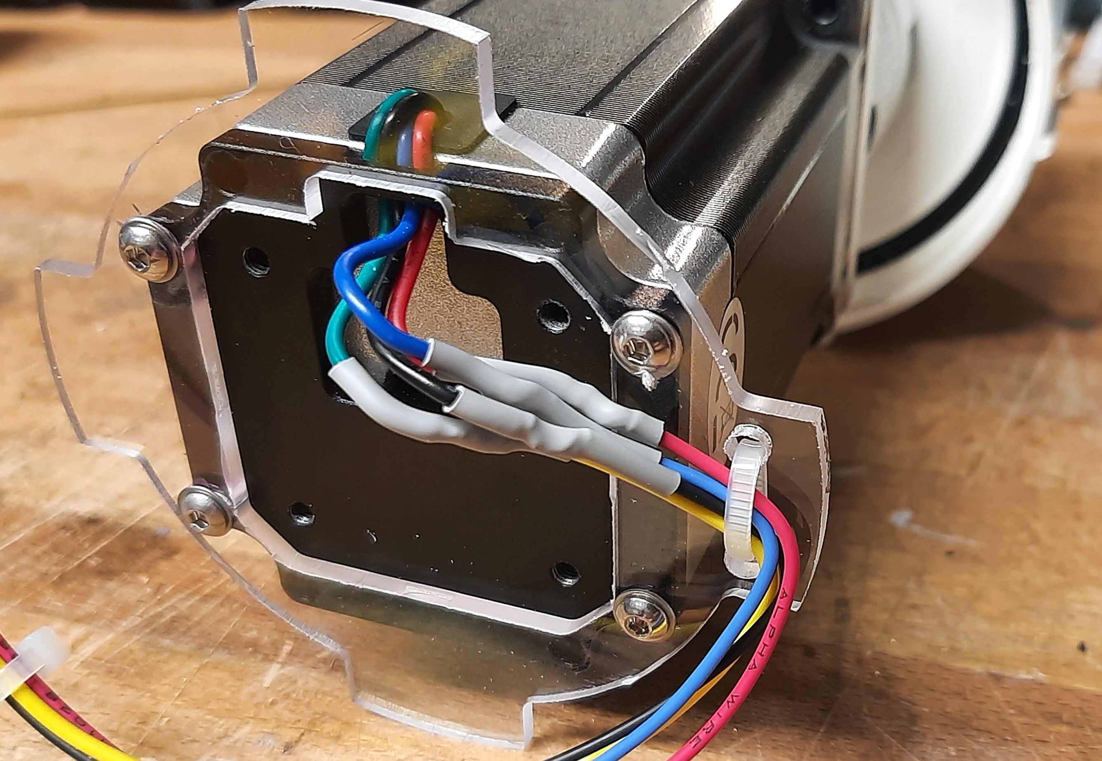
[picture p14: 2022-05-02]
manual/images/winch end wiring.jpg

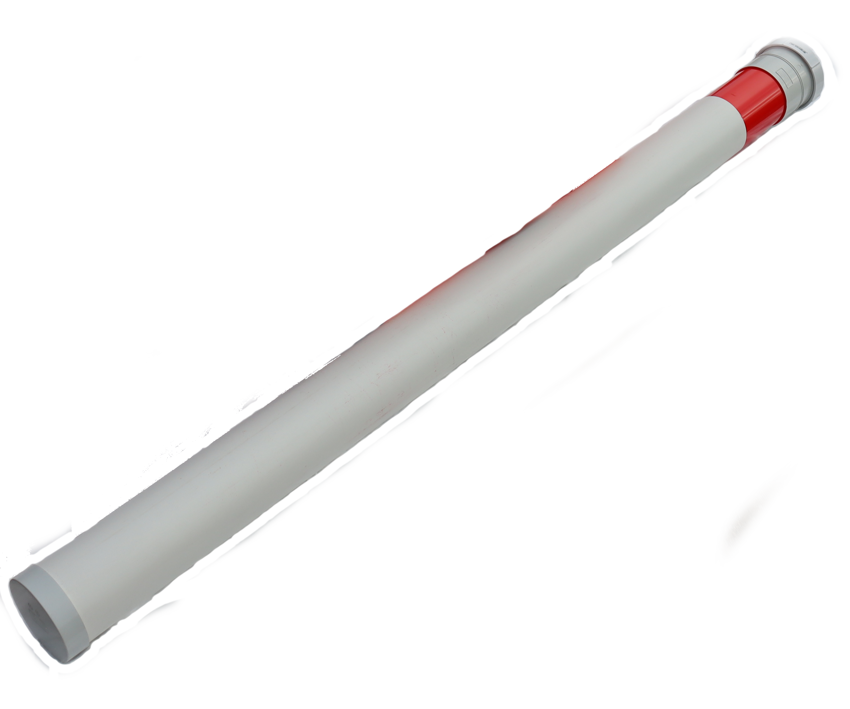
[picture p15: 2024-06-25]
manual/images/tube.png

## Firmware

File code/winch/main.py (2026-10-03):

"""Code to run on the Aqualyd echosounder calibration winches."""

import array # noqa: I001
import time
from sys import stdin, stdout
import xbee
from machine import I2C, WDT
from micropython import kbd_intr
from fram_i2c import _ADDR
from store_value import storeValue

ticAddr = 14  # i2c bus address for the motor controller
version = '1'  # Winch code/hardware id 1 = no FRAM, no i2c

debug = False
monitor = False

# Work out which comms channel to use
uart = True  # Use the UART to control the motor controller
i2c = I2C(1, freq=100000)
devices = i2c.scan()
if _ADDR in devices:  # FRAM device present
    version = '2'  # FRAM, UART
if ticAddr in devices:  # tic device present
    version = '3'  # FRAM, i2c
    uart = False  # use i2c to control the motor controller
    # print('Using i2c - motor controller detected on the bus.')


class TicXbee:
    """Provide access to tic from the xbee."""

    def __init__(self):
        # Get the winch id
        self.addr = int(xbee.atcmd('NI')[-1])
        if uart:
            kbd_intr(-1)  # ignore Ctrl-C (0x03) on UART
        else:
            self.i2c = I2C(1, freq=100000)
        self.max_payload_len = int(xbee.atcmd('NP'))  # for sending over the air


    def send_command(self, c, data_bytes):
        # data_byes should be an iterable data structure
        buf = bytearray([c])
        if data_bytes:
            buf.extend(bytes(data_bytes))

        if uart:
            stdout.buffer.write(buf)
        else:
            self.i2c.writeto(ticAddr, buf)

    def get_variables(self, offset, length):
        if uart:
            self.send_command(0xA1, [offset, length])
            result = stdin.buffer.read(length)
            if result is None:
                result = bytearray([])
        else:
            self.i2c.writeto(ticAddr, bytes([0xA1, offset]))
            result = self.i2c.readfrom(ticAddr, length)
        return result

    def get_velocity(self):
        # Get velocity
        v = tic.get_variables(0x26, 4)  # signed 32-bit
        v = int.from_bytes(v[0:4], 'little')  # microsteps per 10000s
        v = -1 * self.twos_complement(v, 32)
        return v

    def set_velocity(self, velocity, step_mode):
        # A 32-bit write for the velocity
        self.send_command(0xE3, self.encode_32bit(velocity))
        # A 7-bit write for the stepping
        self.send_command(0x94, [step_mode & 127])

    def set_current_limit(self, current):
        # A 7-bit write for the current
        current_value = int(current / 40)
        self.send_command(0x91, [current_value & 127])

    def get_serial_device_number(self):
        n = self.get_variables(0x07, 1)
        return n

    def reset_command_timeout(self):
        self.send_command(0x8C, [])

    def exit_safe_start(self): 
        self.send_command(0x83, [])

    def energize(self):
        self.send_command(0x85, [])

    def halt_and_set_position(self, pos):
        # A signed 32-bit write for the position
        self.send_command(0xEC, self.encode_32bit(pos))

    def encode_32bit(self, v):
        if uart:
            return [((v >> 7) & 1) | ((v >> 14) & 2) |
                    ((v >> 21) & 4) | ((v >> 28) & 8),
                    v >> 0 & 0x7F,
                    v >> 8 & 0x7F,
                    v >> 16 & 0x7F,
                    v >> 24 & 0x7F]

        return [v >> 0 & 0xFF,
                v >> 8 & 0xFF,
                v >> 16 & 0xFF,
                v >> 24 & 0xFF]

    def twos_complement(self, value, bitWidth):

        if value >= 2**bitWidth:
            return value  # should raise an exception here...

        return value - int((value << 1) & 2**bitWidth)

    def get_status(self):
        # Get input voltage
        vin_bytes = self.get_variables(0x33, 2)  # [mV], unsigned 16-bit
        vin = int.from_bytes(vin_bytes, 'little') / 1000

        # Get position & velocity
        state = self.get_variables(0x22, 8)  # 2 x signed 32-bit

        position = int.from_bytes(state[0:4], 'little')  # microsteps
        position = -1 * self.twos_complement(position, 32)

        velocity = int.from_bytes(state[4:8], 'little')  # microsteps per 10000s
        velocity = -1 * self.twos_complement(velocity, 32)

        # Get Xbee internal temperature
        xbee_temp = int(xbee.atcmd('TP'))  # 2's complement
        if xbee_temp > 0x7FFF:
            xbee_temp = xbee_temp - 0x10000

        return (vin, position, velocity, xbee_temp)

    def get_and_send_status(self, send_addr):
        # Get winch status and send it to the controller and any monitors
        (vin, pos_actual, velocity_actual, t) = self.get_status()

        v_physical = velocity_actual * pulses_factor_speed  # [m/s]
        p_physical = pos_actual * pulses_factor_position + pos_offset  # [m]

        try:
            # This value only gets used on startup, when pos_actual is zero, so storing
            # p_physical ensures that on startup, p_physical is the same as on shutdown/power loss.
            pos_store.put(p_physical)
        except Exception:  # noqa: BLE001, S110
            pass

        data = '{},{:.1f},{},{:.2f},{:.2f},{}'.format(winch, vin, t, p_physical,  # noqa: UP032
                                                      v_physical, version)
        if len(data) > self.max_payload_len:
            data = '{}, error - message too long'.format(winch)  # noqa: UP032

        # send to the requested address
        if send_addr is not None:
            try:
                xbee.transmit(send_addr, data)
            except Exception:  # noqa: BLE001, S110
                pass

        # For xbees that advertise themselves as monitors
        if monitor:
            for addr in active_monitors:
                try:
                    xbee.transmit(addr, data)
                except Exception:  # noqa: BLE001, S110
                    pass

def retire_monitors():
    """Remove old monitor addresses."""
    now = time.ticks_ms()

    if debug:
        print('Monitors before retiring: {}'.format(len(active_monitors)))  # noqa: UP032

    for addr, tick in list(active_monitors.items()):
        if time.ticks_diff(now , tick) > max_monitor_age:
            del active_monitors[addr]

    if debug:
        print('Monitors after retiring: {}'.format(len(active_monitors)))  # noqa: UP032


# Config variables

# xbee's that we send status messages to
active_monitors = {}
max_monitor_age = 5000  # [ms]

status_period = 500  # [ms] how often to send status messages
max_motor_current = 2720  # [mA] From motor specs

# Reduce the max allowed motor current when winch is stopped. This significantly
# reduces the power used during a calibration.
current_limit_stationary = 1000  # [mA]

# Given the parameters of the reel and motor, work out step rate needed to get
# the desired line speed range.
min_line_speed = 0.02  # [m/s]
max_line_speed = 1.0  # [m/s]

drum_diameter = 0.070  # [m]
gearbox_ratio = 4.25  # the PG4 gearbox
rotation_per_step = 1.8  # [deg] before gearbox
substep_divider = 0.25  # setting in the motor driver
tic_multiplier = 10000.0  # the tic wants pulse rates to be multiplied by this
speed_steps = 256  # the number of different speeds to offer

step_mode = 2  # 1/4 step

drum_circum = 3.14159 * drum_diameter  # [m]
tic_pulses_per_rev = 360.0/rotation_per_step * gearbox_ratio / substep_divider * tic_multiplier

min_tic_pulses = min_line_speed / drum_circum * tic_pulses_per_rev
max_tic_pulses = max_line_speed / drum_circum * tic_pulses_per_rev

# Use to convert pulses/s and position ticks to m/s and m
pulses_factor_speed = drum_circum / tic_pulses_per_rev
pulses_factor_position = drum_circum / tic_pulses_per_rev * tic_multiplier

pos_offset = 0.0  # [m]
try:
    pos_store = storeValue()
    pos_offset = pos_store.get()
except RuntimeError:
    pos_offset = 0.0  # [m]

# note: there are some speeds that the motor resonates strongly at and for which
# the motor 'jams'. These ranges need to be avoided...
step_tic_pulses = (max_tic_pulses - min_tic_pulses) / (speed_steps-1)

# speed as a signed 32 bit integer. Use array instead of list,
# for efficiency (as per micropython guidelines)
speed = array.array('l', [int(i*step_tic_pulses + min_tic_pulses) for i in range(speed_steps)])

tic = TicXbee()

# and an index into the received messages.
winch = tic.addr  # (1, 2, or 3)

# get the motor controller started
tic.energize()
tic.exit_safe_start()

tic.set_current_limit(current_limit_stationary)

prev_current_limit = current_limit_stationary
velocity_actual = 0

# Extra command chars
action = '_'
winch_id = '_'

wdt = WDT(timeout=2500)  # [ms]

# The micropython receive buffer needs to be emptied before we start processing
# messages, but there is no flush() or similar call.
# The buffer can only hold 4 packets, so just read it 4 times quickly.
for _ in range(4):
    xbee.receive()

then = time.ticks_ms()
controller_addr = None
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

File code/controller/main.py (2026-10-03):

"""Code to run on the Aqualyd echosounder calibration winch wireless control box."""

import gc

import machine

# Status leds. Do these early cause default states of the pin can cause unwanted
# operation of the leds
ledRed = machine.Pin(machine.Pin.board.D15, machine.Pin.OUT, value=0)
ledGreen = machine.Pin(machine.Pin.board.D19, machine.Pin.OUT, value=0)
from max17048 import max17048  # noqa
import time
import xbee
from xbee import relay

# Configurations

debug = False
monitor = False

# Time between checking controls (also the time between sending messages to the winches)
pollInterval = 100  # [ms]

# Used to do things every x'th time through the main loop
loopCount = 0

# How often to toggle the status LED
statusToggleRate = 2  # every nth time through the main loop

# How often to measure and send the controller battery voltage
batteryInterval = 50  # times through the pollInternal loop

# Codes that are sent to the receivers
stop = '0'
up = '2'
down = '1'

# Mode switch states
EXTENDER = 0
CONTROLLER = 1
modeText = ['extender', 'controller']

# if there is no battery gauge, we say that it is empty
bVolt = 0.0  # [V]
bSOC = 0.0  # [%]
bCRate = 0.0  # [%/hr]

# xbee's that we send status messages to
activeMonitors = {}
maxMonitorAge = 5000  # [ms]
retireMonitorInterval = 10  # times through the main loop

# This xbee's node identifier
ident = xbee.atcmd('NI')

# Battery monitoring
try:
    battery = max17048()
except Exception:  # noqa: BLE001
    battery = None


def receive_status(m):
    """Is called when data is received.

    Data either comes from the winches or from a monitoring Xbee
    """
    if m is None:  # no new message
        return

    # pull out the message from the received data
    msg = m['payload'].decode('ascii')

    if msg == 'MONITOR':
        if monitor:
            activeMonitors[m['sender_eui64']] = time.ticks_ms()
        return

    # Is a winch message, so send out on Bluetooth for the app
    if currentMode == CONTROLLER:
        try:
            relay.send(relay.BLUETOOTH, msg)
        except Exception:  # noqa: BLE001, S110
            pass


def send_self_battery(cid, mode, v, soc, rate):
    """Send out the state of the battery in the controller."""
    msg = '0,{},{},{:0.2f},{:0.1f},{:0.1f}'.format(cid, modeText[mode], v, soc, rate)  # noqa: UP032
    try:
        relay.send(relay.BLUETOOTH, msg)
    except Exception:  # noqa: BLE001, S110
        pass

    # For xbee's that advertise themselves as monitors
    if monitor:
        for addr in activeMonitors:
            try:
                xbee.transmit(addr, msg)
            except Exception:  # noqa: BLE001, S110
                pass


def retire_monitors():
    """Remove old monitor addresses."""
    now = time.ticks_ms()
    if debug:
        print('Monitors before retiring: {}'.format(len(activeMonitors)))  # noqa: UP032
    for addr, tick in list(activeMonitors.items()):
        if time.ticks_diff(now , tick) > maxMonitorAge:
            del activeMonitors[addr]
    if debug:
        print('Monitors after retiring: {}'.format(len(activeMonitors)))  # noqa: UP032


def setStatusLED(mode):
    """Set the status LED to indicate the operation mode."""
    if mode == CONTROLLER:
        ledGreen.on()
        ledRed.off()
    elif mode == EXTENDER:
        ledGreen.off()
        ledRed.on()


def flashStatusLED(mode, state):
    """Use to flash the leds on and off."""
    if mode == CONTROLLER:
        ledGreen.value(state)

    if mode == EXTENDER:
        ledRed.value(state)


# Disable pins that aren't used.
machine.Pin(machine.Pin.board.D2, mode=machine.Pin.DISABLED)
machine.Pin(machine.Pin.board.D16, mode=machine.Pin.DISABLED)
machine.Pin(machine.Pin.board.D17, mode=machine.Pin.DISABLED)
machine.Pin(machine.Pin.board.D18, mode=machine.Pin.DISABLED)

# Mode select switch
modeSelect = machine.Pin(machine.Pin.board.D5, machine.Pin.IN, machine.Pin.PULL_UP)

# And set LEDs to reflect this value
currentMode = modeSelect.value()
setStatusLED(currentMode)

# The speed potentiometer
speedPot = machine.ADC(machine.Pin.board.D0)

# Pin definitions for the winches
winch1out = machine.Pin(machine.Pin.board.D10, machine.Pin.IN, machine.Pin.PULL_UP)
winch1in = machine.Pin(machine.Pin.board.D12, machine.Pin.IN, machine.Pin.PULL_UP)
winch2out = machine.Pin(machine.Pin.board.D7, machine.Pin.IN, machine.Pin.PULL_UP)
winch2in = machine.Pin(machine.Pin.board.D9, machine.Pin.IN, machine.Pin.PULL_UP)
winch3out = machine.Pin(machine.Pin.board.D4, machine.Pin.IN, machine.Pin.PULL_UP)
winch3in = machine.Pin(machine.Pin.board.D3, machine.Pin.IN, machine.Pin.PULL_UP)

xbee.receive_callback(receive_status)
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

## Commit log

2021-10-06 Change to match 3d printed drum + simplify speed selection code
2022-02-06 Add schematic for winch cylinder
    [winch box.sch]
2022-02-06 Add controller wiring diagrams
    [controller cut layout.dxf, controller layout.sch, drill guidedxf.dxf]
2022-03-27 Send status message back to controller, change max current per speed
2022-03-29 Change current limit code
2022-03-31 Current reduction only done when stationary. Tweak code layout.
2022-04-01 limit current when requested and actual speed is zero
2022-04-04 change current before changing motor speed
2022-04-05 Change low battery voltage warning level
2022-04-08 Show a running mean of input voltage
2022-04-10 Running mean for temperature; working config dialog
2022-04-25 Remove reporting of current setting value
    was just for debugging purposes
2022-05-02 Current no longer reported
2022-06-29 Update schematics
    [controller layout.sch, winch box.sch]
2022-06-29 Update manual for upgraded system
    Battery power
    Android app
    Removal of Stepperonline motor controller
2022-11-26 update version, tweak assembly instructions
2023-09-14 Changes for PCB version of controller
    Winch 2 pins change
    Controller battery voltage is read via an ADC and send out on bluetooth
2023-10-05 Prototype changes for PCB version of controller
2023-10-19 Implement LED status and battery status
2023-10-26 Updates
    LED flash rate indicates battery SOC
    mode is sent on bluetooth as text now, not integer
    hardware config is set via config file
2023-11-08 Tweaks to battery SOC and LEDs
2023-11-11 Setup LEDS as soon as possible
2023-11-11 battery message was being sent too often
2023-11-15 Changes to work with wired version of controller
2024-03-23 Send battery charge rate to the app
2024-03-27 Send battery message to app immediately when changing mode
2024-04-21 Preliminary support for restoring lineout value after power up
2024-05-13 Not using block devices
2024-06-24 First cut and revising the manual for new capabilities
2024-06-27 Bug fix: motor current wasn't being increased when velocity was non zero
2024-07-02 Refine battery instructions
2024-07-04 Support talking to motor controller with i2c
2025-06-14 remove a debugging print
2025-06-15 Prototype of web browser winch status display
2025-06-30 Support for Monitor device
2025-07-02 flash the led when sending a message out
2025-07-02 Add text about Monitor Xbee devices
2025-07-03 simplify logic flow
2025-07-06 increase WDT time and remove debugging print
